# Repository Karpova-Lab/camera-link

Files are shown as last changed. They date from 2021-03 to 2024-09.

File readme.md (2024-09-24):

# Camera Link
This PCB connects a [Chameleon3 USB3](https://www.flir.com/products/chameleon3-usb3/?model=CM3-U3-31S4C-CS) camera to [pyControl](https://pycontrol.readthedocs.io/en/latest/).
It takes "frame grab" and "sync pulse" signals generated by pyControl and coming out of a [D-Series Breakout Board](https://github.com/Karpova-Lab/pyControl-D-series-Breakout) 
and routes them into the GPIO pins of the camera.

Additionally, the PCB has 3 controllable high power IR LEDs that provide light for the camera to see in the dark.

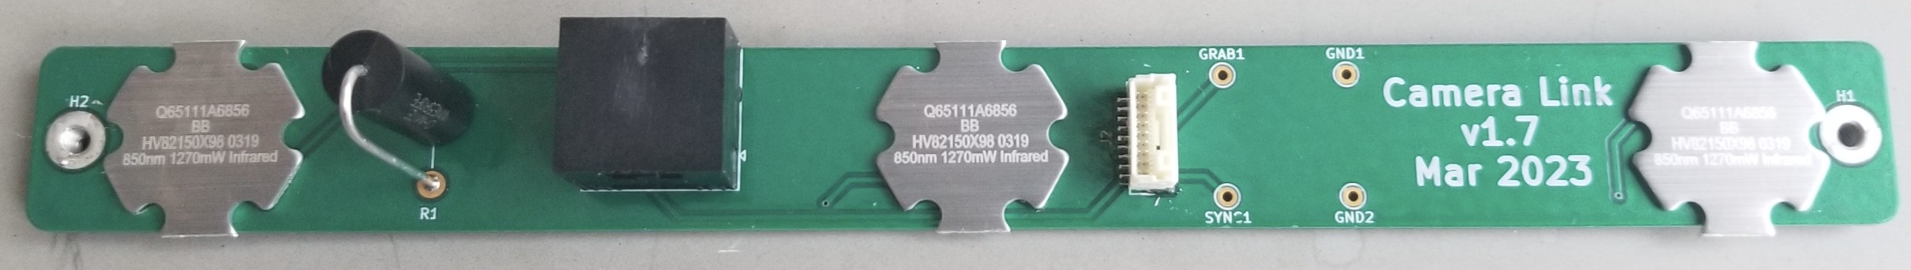
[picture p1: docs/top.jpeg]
top side of PCB

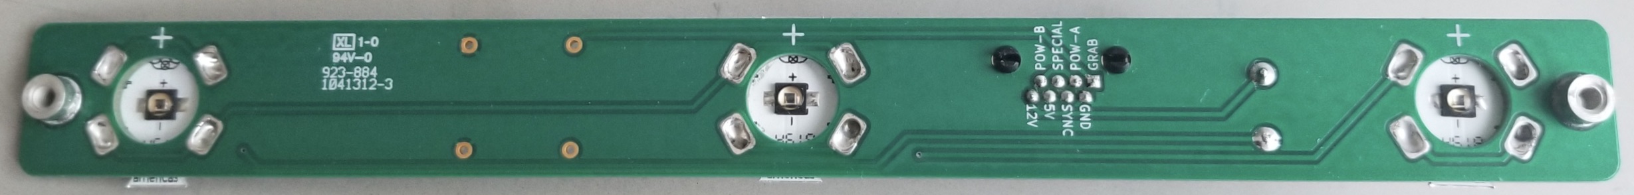
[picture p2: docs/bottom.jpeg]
bottom side of PCB

## PCB 


| Qty | Reference                | Description       | Value/MPN                                                                                                                                    | 
|-----|--------------------------|-------------------|----------------------------------------------------------------------------------------------------------------------------------------------|
| 3   | D1, D2, D3               | 850 nm LED        | [LST1-01F09-IR01-00](https://www.digikey.com/en/products/detail/new-energy/LST1-01F09-IR01-00/9445943?s=N4IgTCBcDaIIwDYDsYC0c4FYAMIC6AvkA)   | 
| 2   | H1, H2                   | Threaded standoff | [24882](https://www.digikey.com/en/products/detail/keystone-electronics/24882/9921822?s=N4IgTCBcDaIMwDYC0YAsAOdYkEYkDkAREAXQF8g)             | 
| 1   | J1                       | 9-pin socket      | [BM09B-NSHSS-TBT](https://www.digikey.com/en/products/detail/jst-sales-america-inc/BM09B-NSHSS-TBT-LF-SN/3313615)                            | 
| 1   | J2                       | RJ45 jack         | [E5J88-00LJG2-L](https://www.digikey.com/en/products/detail/pulse-electronics/E5J88-00LJG2-L/1785312?s=N4IgTCBcDaIKxwMwFoxgGwBZkDkAiIAugL5A) | 
| 1   | R1                       | 5 watt resistor   | [5Ω](https://www.digikey.com/en/products/detail/ohmite/WNE5R0FET/3114558?s=N4IgTCBcDaIOoDkCiBWATgBgGYFMAuAxniALoC%2BQA)                      | 

[View interactive BOM](https://karpova-lab.github.io/camera-link/ibom)

## Camera Hardware
- [CM3-U3](docs/CM3-U3-Technical-Reference.pdf) camera
- [A4Z2812CS-MPIR](docs/A4Z2812CS-MPIR_12-14.pdf) lens

## GPIO cable
- [9 position NSH series plug](https://www.digikey.com/en/products/detail/jst-sales-america-inc/NSHR-09V-S/3313624)
- [8" pre-crimped wires](https://www.digikey.com/en/products/detail/jst-sales-america-inc/ASSHLSSHL28K203/9924242?s=N4IgjCBcoOw1oDGUBmBDANgZwKYBoQB7KAbRACYAOcgBgFYBmEAXQIAcAXKEAZQ4CcAlgDsA5iAC+BGJQQhkkdNnxFS4AGwM6MdS3ZdIvASPFSQDMPGjzUmXAWKQyAFhrOds1iE7c+QsZIEALQQ1gpK9qpOIM50dCxmQc5y4XYqjmRg6mD0CRISQA)

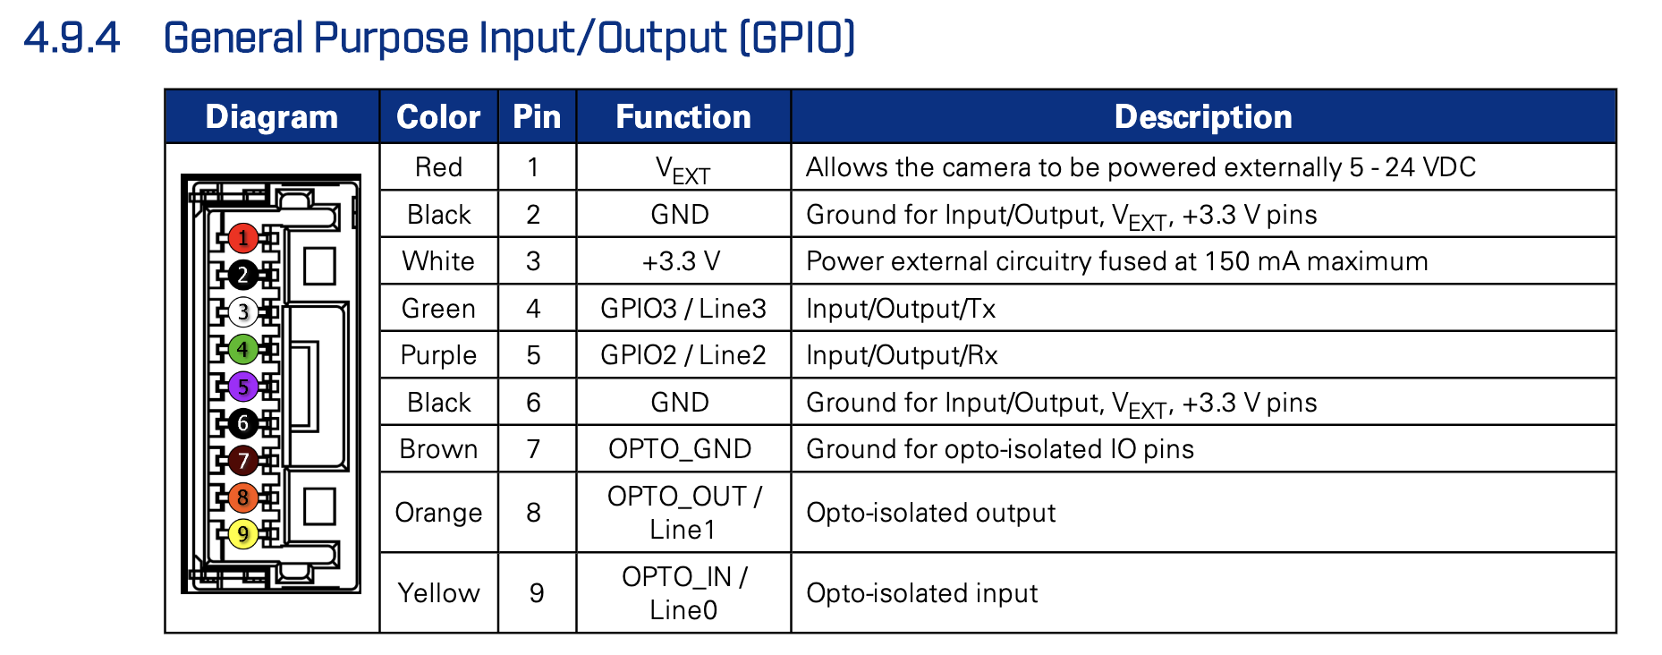
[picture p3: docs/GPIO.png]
camera GPIO

| GPIO pin | GPIO Color | GPIO Function | RJ45 Pin | pyControl Function | Purpose                                                  |
|----------|------------|---------------|----------|--------------------|----------------------------------------------------------|
| 4        | Green      | GPIO3/Line3   | 1        | DIO_A              | pyControl sends square wave to camera to grab each frame |
| 9        | Yellow     | OPTO_IN/Line0 | 4        | DIO_B              | pyControl sends random sync pulse                        |
| 6        | Black      | GND           | 2        | Ground             | Ground                                                   |
| 7        | Brown      | OPTO_GND      | 2        | Ground             | Ground                                                   |

## Software
- [Bias](https://github.com/iorodeo/bias)
- [pyControl synchronization](https://pycontrol.readthedocs.io/en/latest/user-guide/synchronisation/)

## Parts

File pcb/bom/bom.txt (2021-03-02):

"Qty","Reference","Description","Value/MPN","Purchase Link"
"24","D1, D2, D3, D4, D5, D6, D7, D8, D9, D10, D11, D12, D13, D14, D15, D16, D17, D18, D19, D20, D21, D22, D23, D24","850nm 140˚ LED","LED","https://www.digikey.com/en/products/detail/15412085BA400/732-15412085BA400CT-ND/12385059?itemSeq=350631554"
"2","H1, H2","Threaded standoff","24882","https://www.digikey.com/en/products/detail/keystone-electronics/24882/9921822?s=N4IgTCBcDaIMwDYC0YAsAOdYkEYkDkAREAXQF8g"
"1","J1","RJ45 jack","0855025008","https://www.digikey.com/en/products/detail/molex/0855025008/2404887?s=N4IgTCBcDaIOoFkDMBWALAdgMIBUC0AcgCIgC6AvkA"
"1","J2","","Screw_Terminal_01x08","~"
"1","R1","1206 Resistor","10Ω","https://www.digikey.com/en/products/detail/bourns-inc/CMP1206AFX-10R0ELF/12333667?s=N4IgTCBcDaIMIFkAKBGMAGAbAQQGIA0BaFdAJXQFEAZXEAXQF8g"

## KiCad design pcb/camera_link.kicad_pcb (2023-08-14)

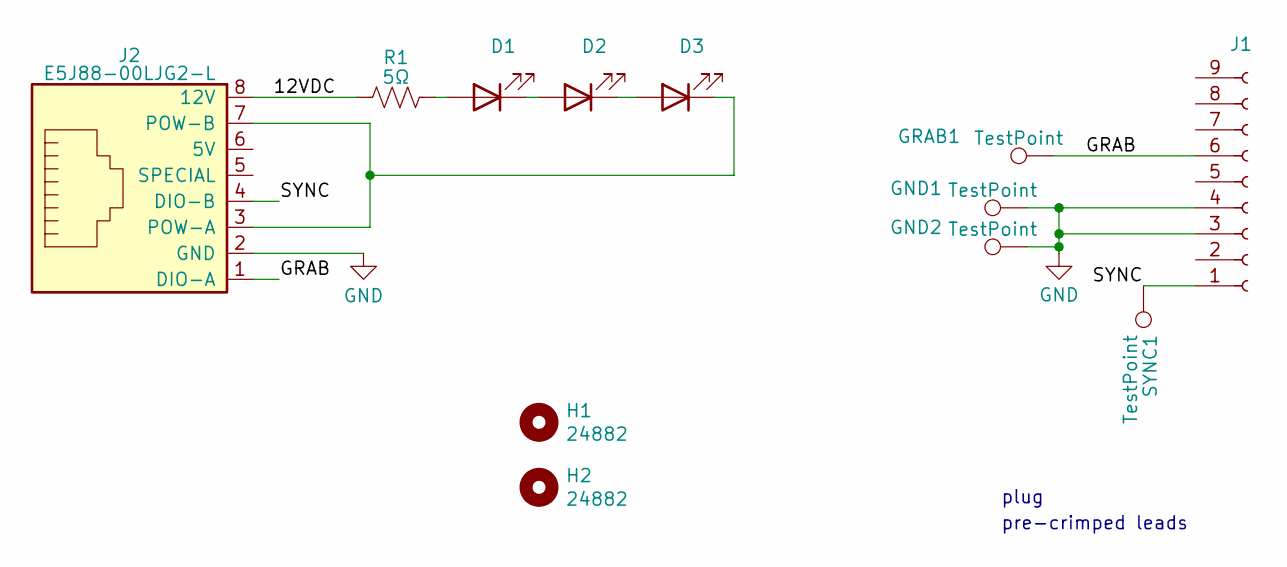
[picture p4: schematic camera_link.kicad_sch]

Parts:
D1, D2, D3: LST1-01F09-IR01-00; LED_starboard
GND1, GND2: TestPoint; Pin_D1.0mm_L10.0mm
GRAB1: TestPoint; Pin_D1.0mm_L10.0mm
H1, H2: 24882; standoff_nut
J1: BM09B-NSHSS-TBT; JST_NSH_1x09_VERTICAL
J2: E5J88-00LJG2-L; RJ45_THP_tab_on_top
R1: 5Ω; R_Axial_DIN0614_L14.3mm_D5.7mm_P7.62mm_Vertical
SYNC1: TestPoint; Pin_D1.0mm_L10.0mm

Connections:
/12VDC: J2.8 (12V), R1.1
/GRAB: GRAB1.1, J1.6, J2.1 (DIO-A)
/SYNC: J1.1, J2.4 (DIO-B), SYNC1.1
GND: GND1.1, GND2.1, J1.3, J1.4, J2.2 (GND)
unnamed: D1.2 (A), R1.2
unnamed: D1.1 (K), D2.2 (A)
unnamed: D2.1 (K), D3.2 (A)
unnamed: D3.1 (K), J2.3 (POW-A), J2.7 (POW-B)

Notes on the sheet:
pre-crimped leads
plug

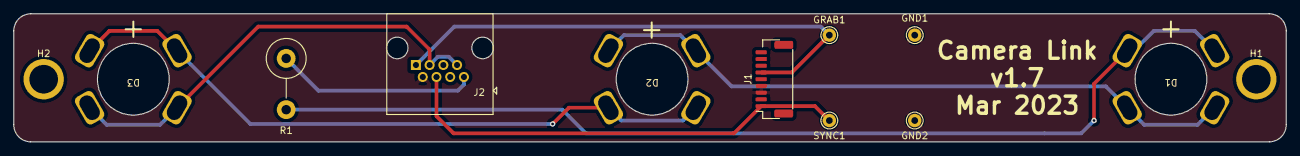
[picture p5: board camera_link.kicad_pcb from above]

Board: 2 copper layers, 189.2 x 19.0 mm, 12 parts (0 on the bottom side), 8 nets.

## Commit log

2021-01-11 PCB v1.1
    [camera_link.kicad_pcb, camera_link.kicad_sch]
2021-03-02 Added gerbers and BOM
    [bom.xlsx]
2021-03-02 update readme
    added PCB link
2022-12-02 pcb v1.3
    [camera_link.kicad_pcb, camera_link.kicad_sch]
2023-01-04 pcb v1.5
    [camera_link.kicad_pcb, camera_link.kicad_sch]
2023-01-12 PCB v1.6
    [camera_link.kicad_pcb, camera_link.kicad_sch]
2023-05-24 pcb v1.7
    [camera_link.kicad_pcb, camera_link.kicad_sch]
2024-09-24 readme update
    - replaced broken lens link with link to datasheet
